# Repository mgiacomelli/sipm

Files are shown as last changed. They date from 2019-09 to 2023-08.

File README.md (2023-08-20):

**This page is obsolete.  A greatly improved design is available here: https://github.com/OpenSiPM/sipm-bias-control**

The updated design has higher dynamic range, lower noise, higher bandwidth and includes the bias generation, power supplies and low pass filter.  

# Introduction

These are the design files for the SIPM amplifier described in M. G. Giacomelli, "Evaluation of silicon photomultipliers for multiphoton and laser scanning microscopy," J. Biomed. Opt. 24, 1 (2019) available from https://www.spiedigitallibrary.org/journals/journal-of-biomedical-optics/volume-24/issue-10/106503/Evaluation-of-silicon-photomultipliers-for-multiphoton-and-laser-scanning-microscopy/10.1117/1.JBO.24.10.106503.full?SSO=1.  

The design is a relatively low cost, single photon sensitive fluorescense detector using the S14420 silicon photomultiplier from Hamamatsu, which is a TO-5 mounted detector with high QE from 500-700nm.  Compared to a PMT the S14420 has higher effective quantum efficiency (especially above 600nm) but higher dark counts.  

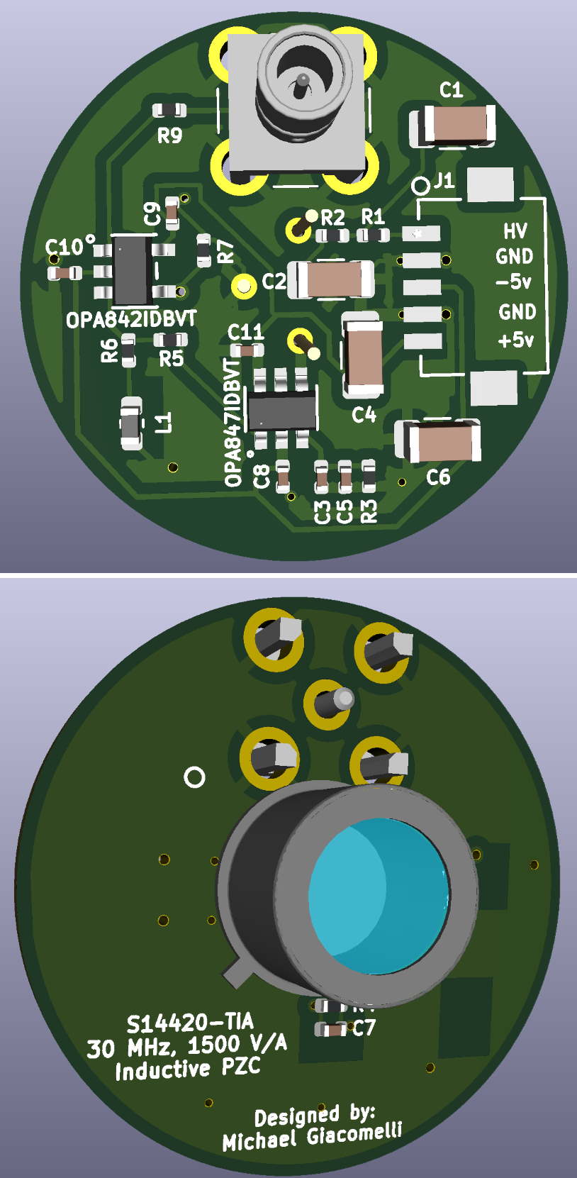
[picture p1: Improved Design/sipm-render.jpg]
Image of SIPM


# Files

The 'Old Gerbers' folder contains the exact gerber files used to manufacture the boards in the manuscript.  The Improved Design folder has KiCAD and gerber files for an updated version of that design that has a few improvements.  In addition, since the design files are present, you can make changes to the design as needed using the open source EDA software KiCAD.  If you only want to make a board, you can upload either set of Gerber files directly to JLCPCB, SEEED, etc.  

# Setting up KiCAD

This project was designed using the current development (5.99) branch of KiCAD, so you must be running that or newer.  Windows builds are available here: 
https://kicad-downloads.s3.cern.ch/index.html?prefix=windows/nightly/

# Ordering boards

Go to https://jlcpcb.com/ or https://www.seeedstudio.com/fusion_pcb.html or the service of your choice, upload the Gerber files, choose 2 layer, and pay.  At present prices, 10 boards will cost about 15-20 dollars shipped to most of the world.  

# Bill of materials

An interactive BOM tool is available here to make placing and ordering compnents easy:  http://htmlpreview.github.io/?https://github.com/mgiacomelli/sipm/blob/master/Improved%20Design/KiCAD/bom/ibom.html

In addition, you will need the matching power cable.  The part is DF13-5S-1.25C, and unless you have the matching crimp tool, you will need 5x H4BBT-10112-R8 pre-crimped leads.  I recommend getting multiple colors as mixing up the wires will destroy your board.  

# Assembly

The easiest way to assemble these boards is using solder paste and a reflow oven.  The inexpensive T-962 clones on Amazon will work fine for simple boards such as this.  Alternatively, they can also be manually soldered.  The design uses a mix of 0402 and larger parts, which can be challenging to solder with the wrong tools.  A ~0.6-1.2mm diameter chissel type soldering tip, high quality no clean flux such as amtech nc-559-v2-tf, 40/60 lead solder, and good tweezer such as Hakko CHP 5-SA or equivilent are strongly recommended if reflow is not used. These are inexpensive and readily available on Amazon. 

# Circuit design

Both the old and improved designs are a 1500 V/A transimpedance amplifier paired with a pole zero compensation (PZC) circuit.  Both PZCs have the same frequency cut on.  The old design uses a capacitive PZC.  While more obvious, this design is problematic because the capacitance of the PZC loads the amplifier.  The original design put an isolation resistor before the capacitance, but this design halves the gain and is less stable.  The improved design implements the same filter but using an inductor.  As a result the resistor and reactive element are flipped, meaning that the opamp is not directly connected to the reactive element and so the isolation resistor is not needed. Therefore gain is doubled.  Further since the PZC resistance is larger, stability is improved.  

# PZC

The values of L1, R5 and R6 define the PZC cut on and amplitude.  These values were near optimal for a previous board iteration, however, the PZC is very sensitive to the exact values so you may find that to hit very high bandwidth (40-50 MHz) or very flat pass band that the values must be adjusted.  Essentially the PZC is adding a gain that compensates for the frequency roll off caused by the RC time constant associated with the individual SIPM cell recharge through the quenching resistors, so adjusting L1 changes at what frequency the added gain kicks in, while changing the values of the resistors lets you change the strength of that gain.  By setting the values carefully, you can cancel out the recharge time of the individual APDs and greatly extend the bandwidth of the detector, often by a factor of 10 or more.  

A more intuitive explination of the PZC method is described in this article:
A. Gola, C. Piemonte, and A. Tarolli, "Analog circuit for timing measurements with large area sipms coupled to lyso crystals," IEEE Trans. Nucl. Sci. 60, 1296–1302 (2013).

# Low pass filter

It is important to add an external low pass filter, either in your ADC or inline with it to reject out of band noise.  If you do not have a suitable lowpass on your ADC, the minicircuits BLP-25 is a reasonable choice with relatively little group delay in the pass band:  https://www.minicircuits.com/WebStore/dashboard.html?model=BLP-25%2B

The bandwidth of a laser scanner is 0.312 times the scan velocity (in meters per second) divided by the spot size (also in meters).  It is a good idea to reduce the bandwidth of the detector as needed with a smaller low pass filter if you do not require 25 MHz at your scan speed.  This will reduce electronic noise.    

# Gain

Total transimpedance gain (as configured, you can adjust it) is 1500 ohms.  There is an additional factor of 2 gain in the OPA842 stage, but this merely compensates for the attenuation caused by the 50 Ohm output impedance.  In addition, the PZC attenautes by a factor of R6/R5 (about 8:1).  Thus peak ampltidue per photon at +5Vbr should be about 4.5mV.  

# Mounting

The entire board is 1 inch across and will mount in an SM1 lens tube:  https://www.thorlabs.com/newgrouppage9.cfm?objectgroup_id=3307

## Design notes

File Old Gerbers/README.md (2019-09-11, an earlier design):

# sipm
Design files for SIPM boards

BOM is here:  https://github.com/mgiacomelli/sipm/blob/master/TiaV3_BOM.xlsx

These are Gerber files for a SIPM+TIA detector board.  I'll update these eventually with a KiCAD design files when I have time to port over to KiCAD.  In the meantime, if you have questions or want to modify the design, contact me and I can help with that.

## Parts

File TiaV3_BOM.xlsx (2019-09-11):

Comment | Description | Name | Footprint | Quantity | Comment
0.10µF | CAP CER 0.1UF 200V X7R 0603 | C1, C5, C7, C9, C20, C21 | SMD-0603C | 6 | MUST use high voltage (>100V) caps for SIPM bias
3.9pF | CAP CER 3.9PF 50V NP0 0603 | C2 | SMD-0603C | 1
0.10µF | CAP CER 1UF 250V X7R 1206 | C3 | SMD-1206C | 1 | MUST use high voltage (>100V) caps for SIPM bias
4.7µF | CAP CER 4.7UF 25V X5R 1206 | C6, C10 | SMD-1206C | 2
100pF | CAP CER 100PF 50V NP0 0603 | C8 | SMD-0603C | 1
43pF | CAP CER 43PF 50V NP0 0603 | C23 | SMD-0603C | 1
0pf | Omitted | C? | SMD-0603C | 1
DF13-5P-1.25DSA | Power Connector | J1 | CON5_1X5_U_DF13 | 1 | Could substitute for through hole
SMB | SMB Straight Connector | P1 | SMB_V-RJ45 | 1
49.9 | RES SMD 49.9 OHM 1% 1/10W 0603 | R1 | SMD-0603-RES | 1 | Use thin film resistors only
1500 | RES SMD 1500 OHM 1% 1/10W 0603, RES SMD 750 OHM 1% 1/4W 0603 | R2, R3 | SMD-0603-RES | 2 | Use thin film resistors only
36 | RES SMD 36 OHM 1% 1/10W 0603 | R11, R? | SMD-0603-RES | 2 | Use thin film resistors only
422 | RES SMD 422 OHM 1% 1/10W 0603 | R20 | SMD-0603-RES | 1 | Use thin film resistors only
82 | RES SMD 82 OHM 1% 1/10W 0603 | R21 | SMD-0603-RES | 1 | Use thin film resistors only
50 | RES SMD 50 OHM 1% 1/10W 0603 | R22 | SMD-0603-RES | 1 | Use thin film resistors only
390 | RES SMD 490 OHM 1% 1/10W 0603 | R23 | SMD-0603-RES | 1 | Use thin film resistors only
75 | RES SMD 75 OHM 1% 1/10W 0603 | Riso | SMD-0603-RES | 1 | Larger values may be needed if unstable
SIPM | S14420-3025MG | S1 | TO-39 | 1
OPA847IDBVT | TI OPAMP | U2 | DBV6 | 1
OPA843IDBVT | Wideband, Low Distortion, Unity Gain Stable, Voltage Feedback Operational Amplifier, 7 to 12 V, -40 to 85 degC, 5-pin SOT23 (DBV5), Green (RoHS & no Sb/Br) | U? | TI-DBV5_N | 1 | Lower gain may be needed depending on A/D range, if R20/R21 < 4, switch to OPA842
Note: All parts are in the digikey catalog except for the SIPM

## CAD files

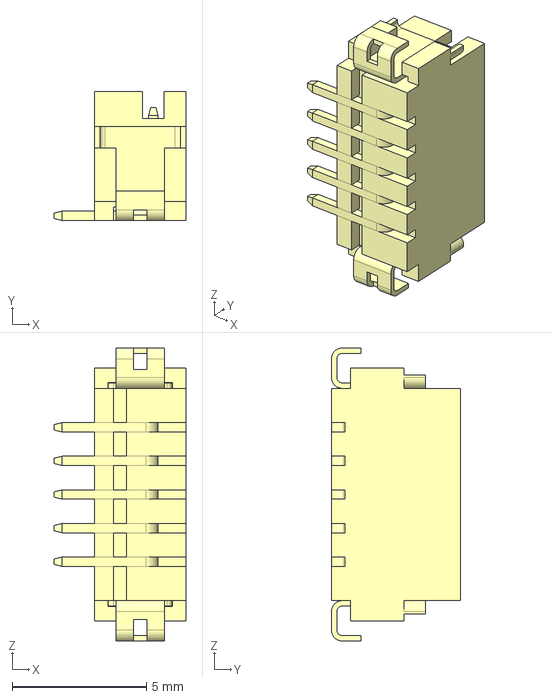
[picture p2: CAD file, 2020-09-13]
Improved Design/KiCAD/step/DF13C-5P-1.25V.stp
4.90 x 4.80 x 10.9 mm

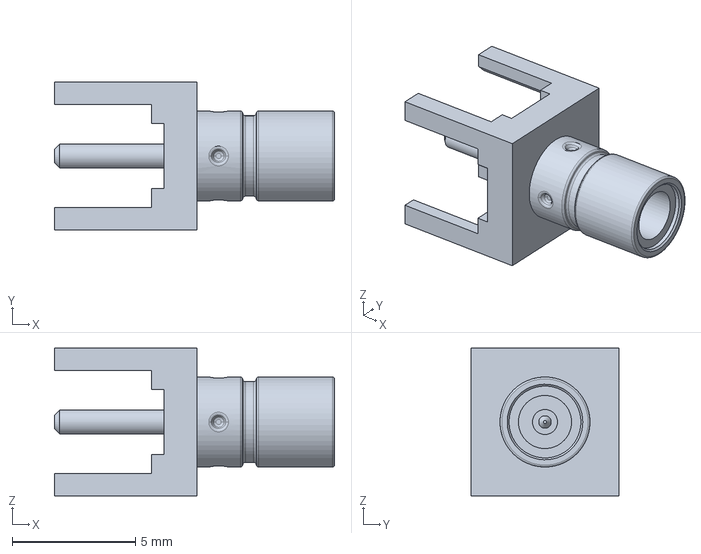
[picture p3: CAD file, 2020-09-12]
Improved Design/KiCAD/step/131-3701-261.stp
11.4 x 5.99 x 5.99 mm

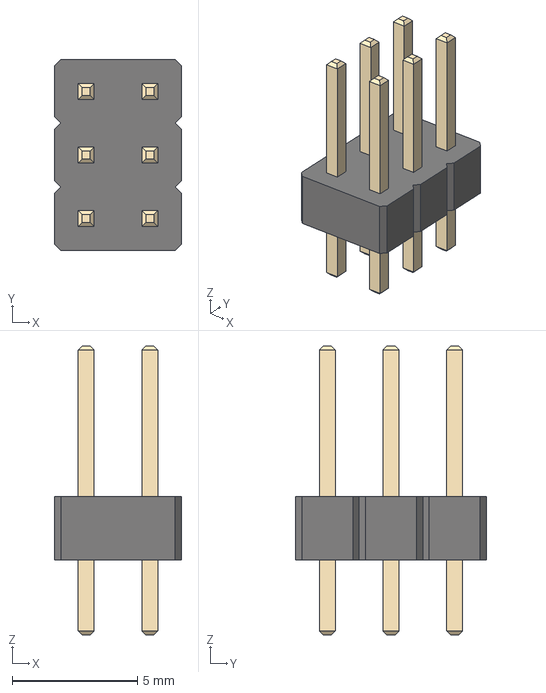
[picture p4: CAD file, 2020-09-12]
Improved Design/KiCAD/step/PinHeader_2x03_P2.54mm_Vertical.step
5.08 x 7.62 x 11.5 mm

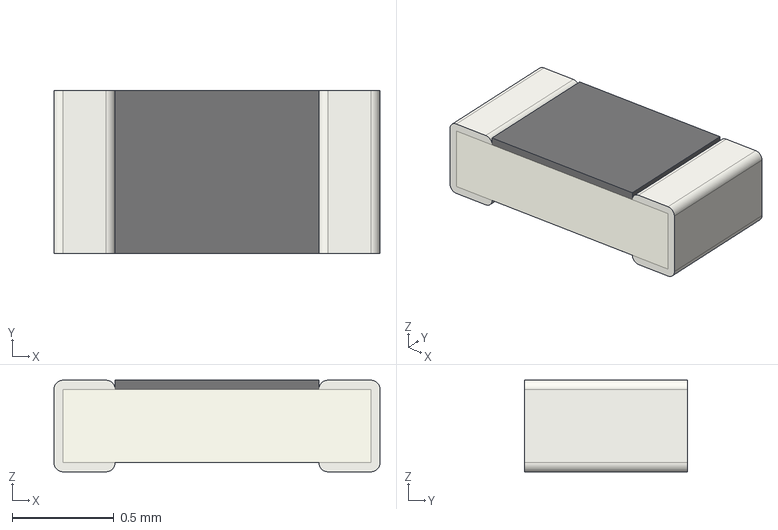
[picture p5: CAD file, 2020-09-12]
Improved Design/KiCAD/step/R_0603_1608Metric.step
1.60 x 0.8 x 0.45 mm

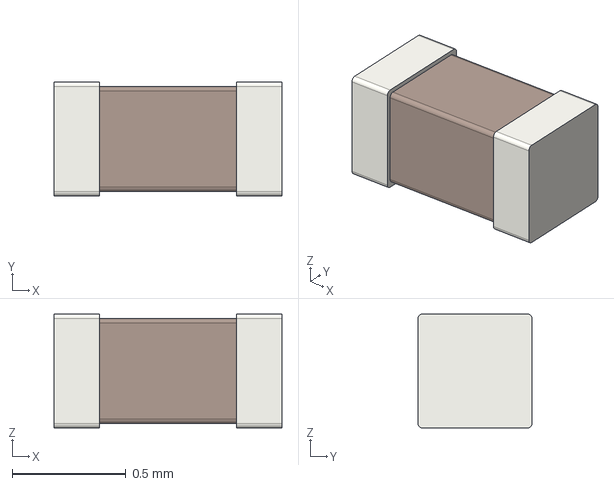
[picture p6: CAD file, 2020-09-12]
Improved Design/KiCAD/step/C_0402_1005Metric.step
1.00 x 0.5 x 0.5 mm

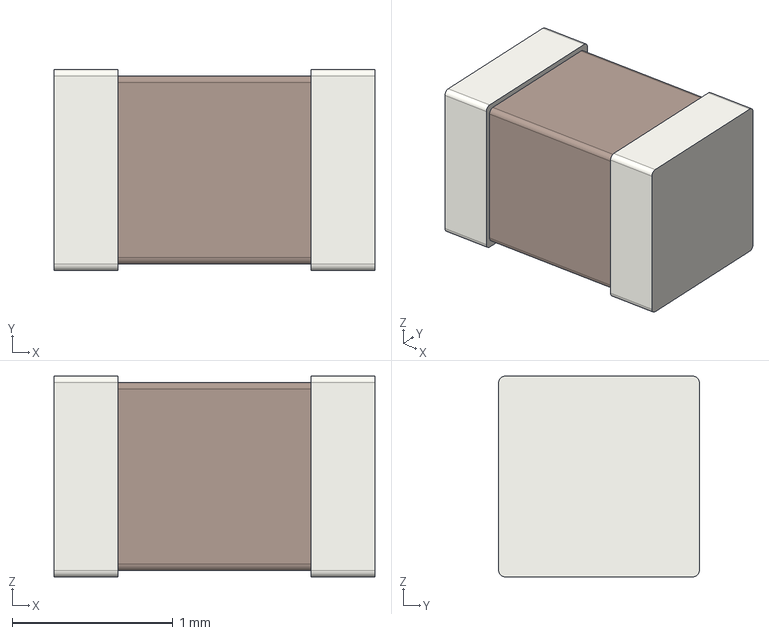
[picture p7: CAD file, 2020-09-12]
Improved Design/KiCAD/step/C_0805_2012Metric.step
2.00 x 1.25 x 1.25 mm

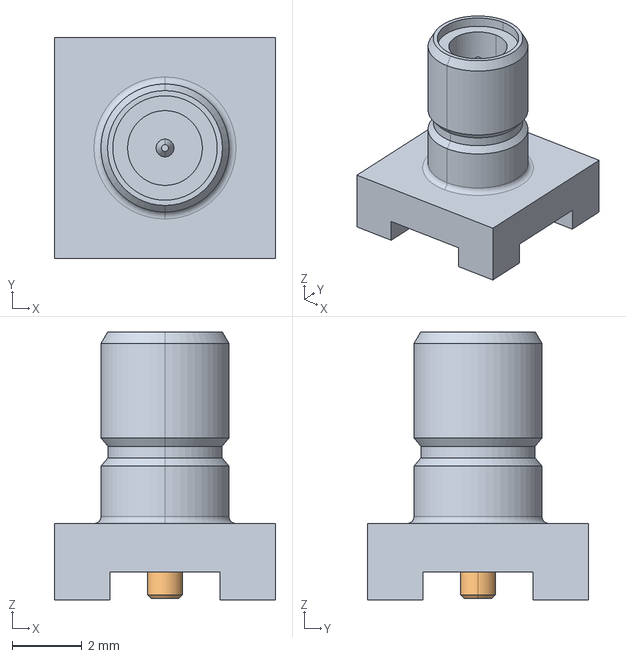
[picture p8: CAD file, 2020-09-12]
Improved Design/KiCAD/step/c-1-1337604-0-d-3d.stp
6.35 x 6.35 x 7.70 mm

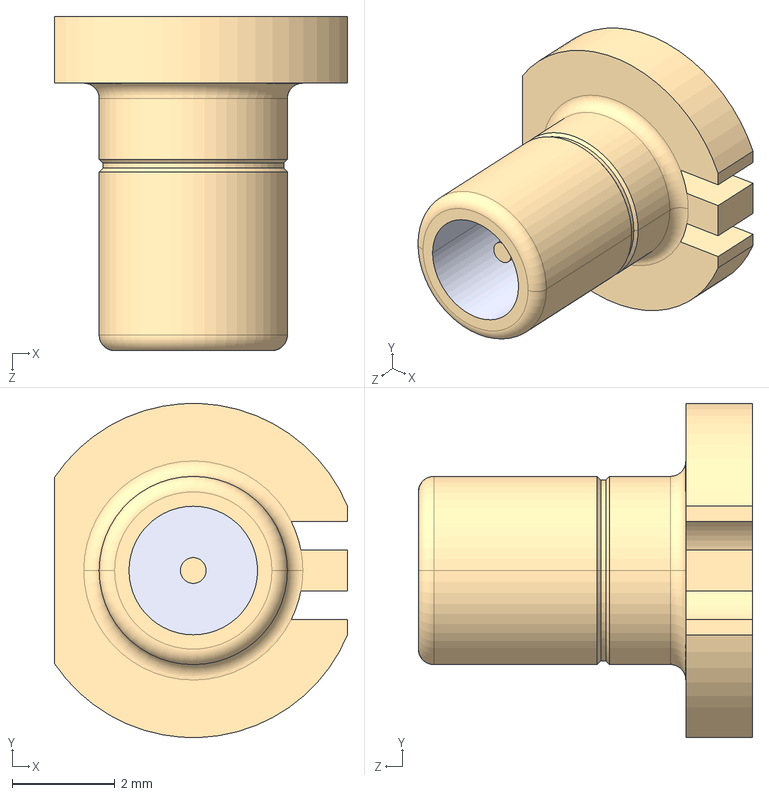
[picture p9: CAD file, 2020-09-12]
Improved Design/KiCAD/step/SMBR004D00.step
5.70 x 6.49 x 6.50 mm

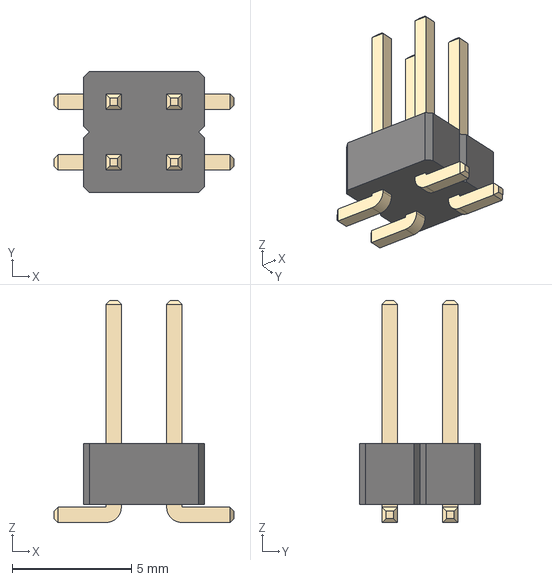
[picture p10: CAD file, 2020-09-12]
Improved Design/KiCAD/step/PinHeader_2x02_P2.54mm_Vertical_SMD.step
7.54 x 5.08 x 9.30 mm

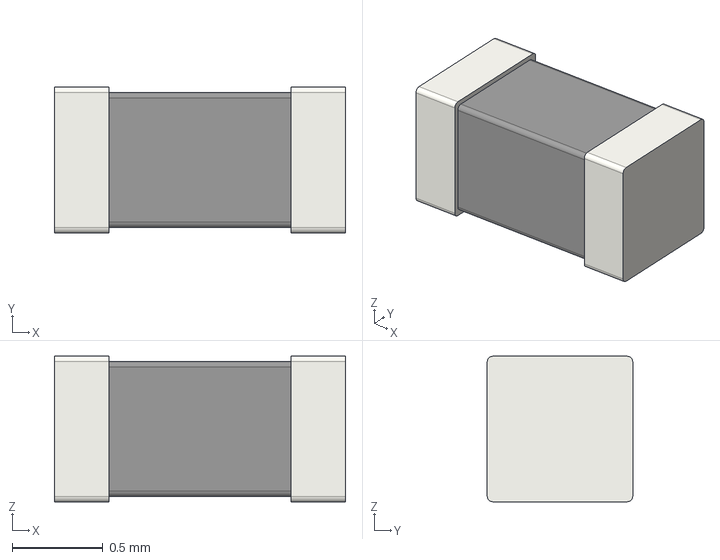
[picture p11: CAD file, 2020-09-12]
Improved Design/KiCAD/step/L_0603_1608Metric.step
1.60 x 0.8 x 0.8 mm

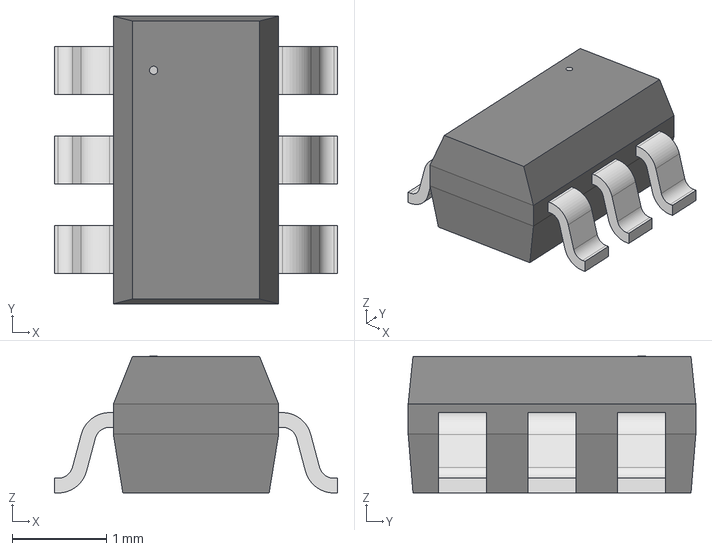
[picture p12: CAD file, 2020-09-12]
Improved Design/KiCAD/step/DBV6.step
3.00 x 3.05 x 1.45 mm

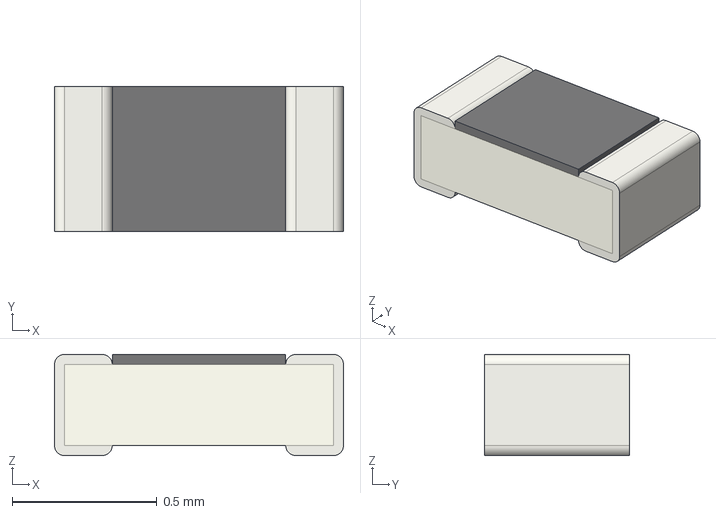
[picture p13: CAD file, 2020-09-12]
Improved Design/KiCAD/step/R_0402_1005Metric.step
1.00 x 0.5 x 0.35 mm

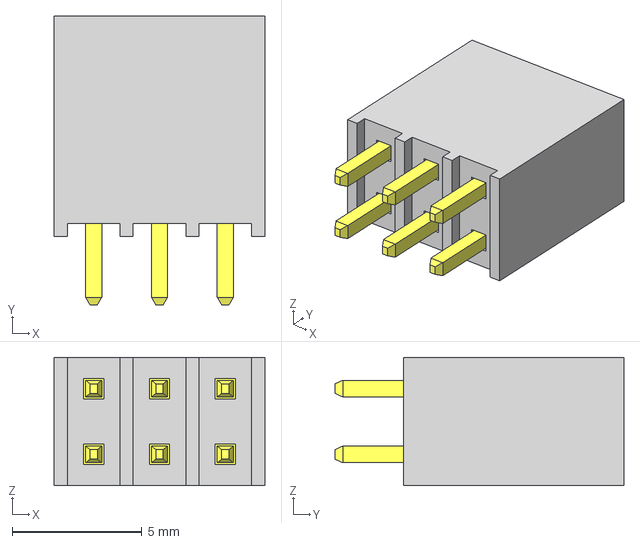
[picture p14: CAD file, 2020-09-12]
Improved Design/KiCAD/step/SSQ-103-01-G-D.step
8.13 x 11.2 x 4.95 mm
_T1SSQ-103-01-G-D
_P2SSQ-103-01-G-D

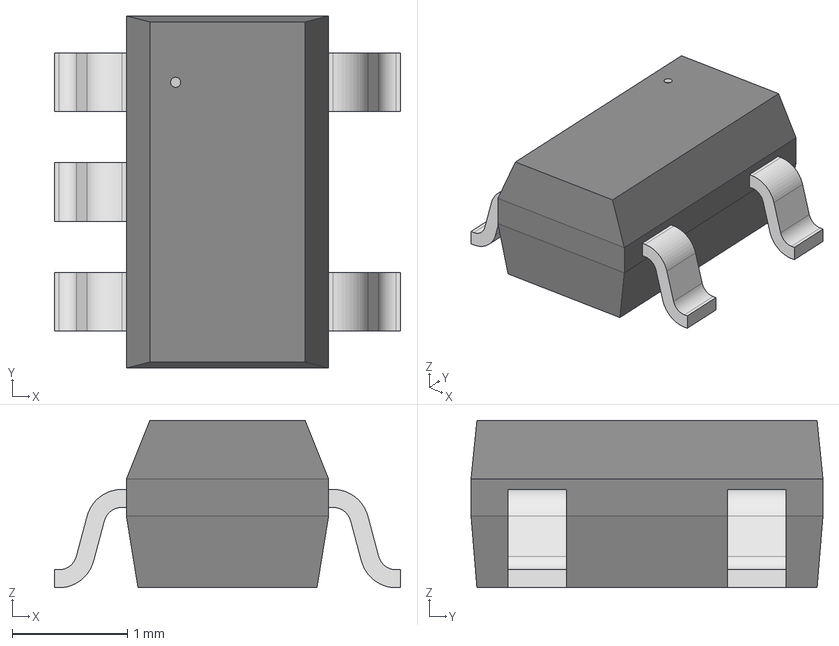
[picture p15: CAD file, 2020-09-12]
Improved Design/KiCAD/step/DBV5.step
3.00 x 3.05 x 1.45 mm

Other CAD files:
Improved Design/KiCAD/step/C_0603_1608Metric.step
Improved Design/KiCAD/step/73415-2061.stp
Improved Design/KiCAD/step/SMBR004D00.SLDPRT

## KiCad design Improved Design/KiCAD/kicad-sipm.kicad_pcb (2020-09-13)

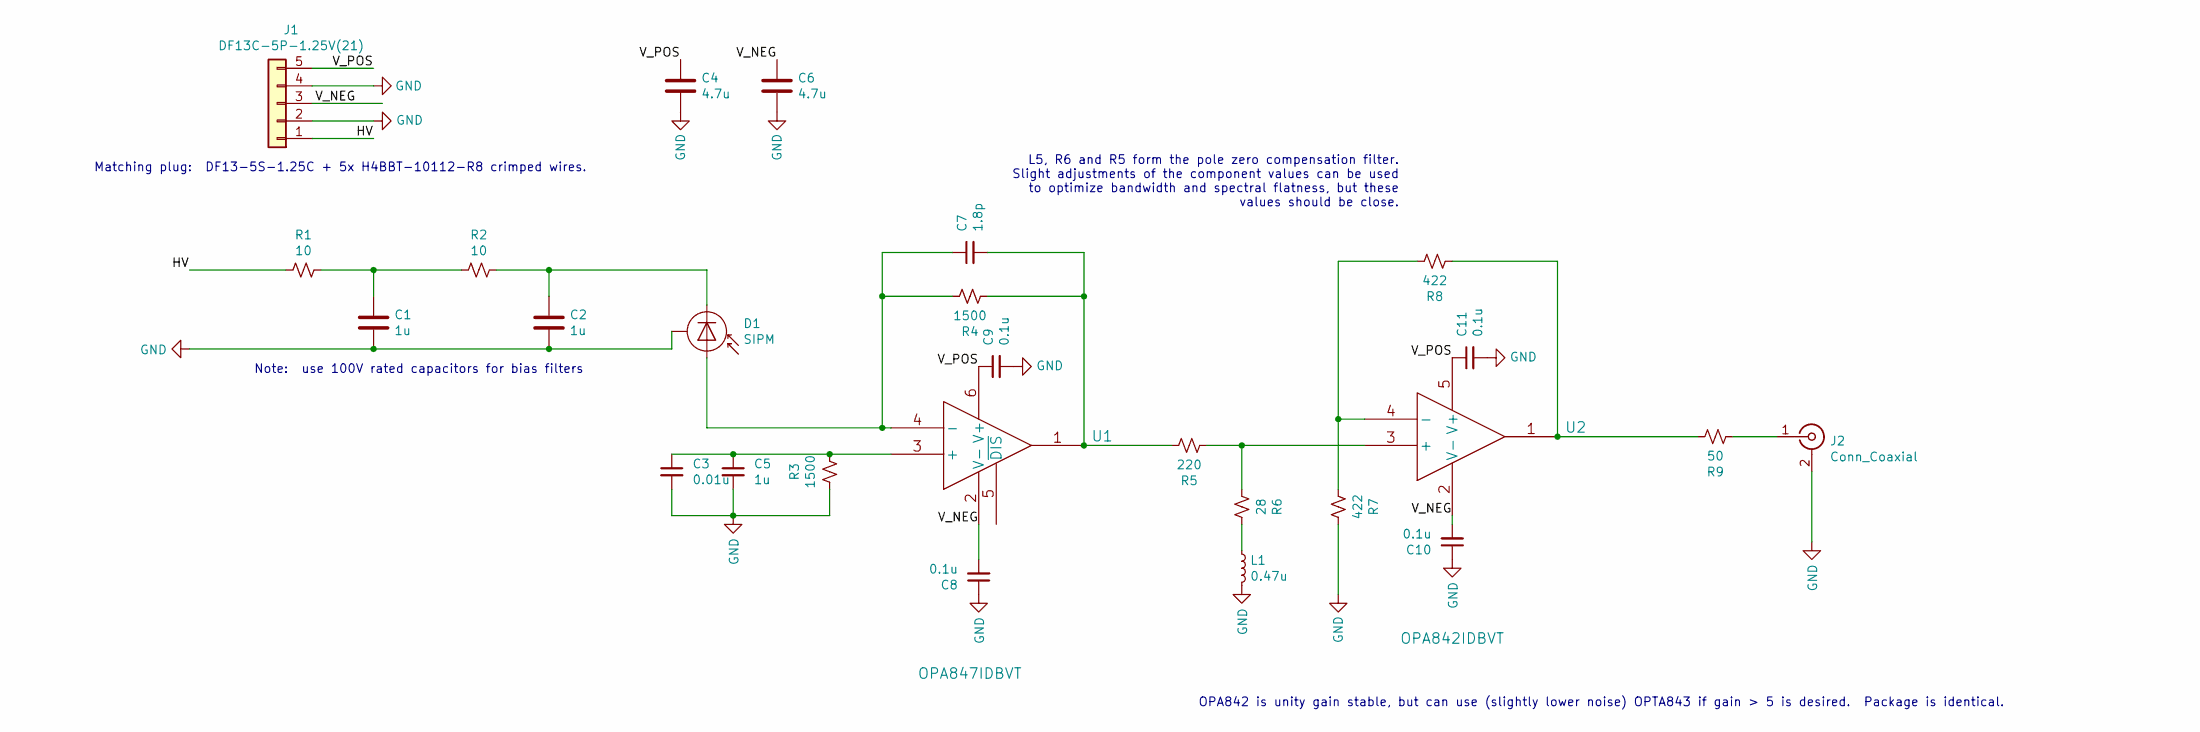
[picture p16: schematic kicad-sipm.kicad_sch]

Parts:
C1, C2: 1u; C_1206_3216Metric
C3: 0.01u; C_0402_1005Metric
C4, C6: 4.7u; C_1206_3216Metric
C5: 1u; C_0402_1005Metric
C7: 1.8p; C_0402_1005Metric
C8, C9, C10, C11: 0.1u; C_0402_1005Metric
D1: SIPM; S14420
J1: DF13C-5P-1.25V(21); DF13C-5P-1.25V21; Digikey Part H126001CT-ND
J2: Conn_Coaxial; SMB_Jack_Vertical
L1: 0.47u; L_0603_1608Metric
R1, R2: 10; R_0402_1005Metric
R3, R4: 1500; R_0402_1005Metric
R5: 220; R_0402_1005Metric
R6: 28; R_0402_1005Metric
R7, R8: 422; R_0402_1005Metric
R9: 50; R_0402_1005Metric
U1: OPA847IDBVT
U2: OPA842IDBVT; OPA843IDBVT

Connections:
/HV: J1.1, R1.1
/V_NEG: C6.1, C8.2, C10.2, J1.3, U1.2 (V-), U2.2 (V-)
/V_POS: C4.1, C9.1, C11.1, J1.5, U1.6 (V+), U2.5 (V+)
GND: C1.2, C2.2, C3.2, C4.2, C5.2, C6.2, C8.1, C9.2, C10.1, C11.2, D1.3 (CASE), J1.2, J1.4, J2.2 (Ext), L1.2, R3.1, R7.2
unnamed: C1.1, R1.2, R2.1
unnamed: C2.1, D1.1 (K), R2.2
unnamed: C3.1, C5.1, R3.2, U1.3 (+)
unnamed: C7.1, D1.2 (A), R4.2, U1.4 (-)
unnamed: C7.2, R4.1, R5.2, U1.1
unnamed: J2.1 (In), R9.1
unnamed: L1.1, R6.2
unnamed: R5.1, R6.1, U2.3 (+)
unnamed: R7.1, R8.2, U2.4 (-)
unnamed: R8.1, R9.2, U2.1

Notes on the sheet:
Note: use 100V rated capacitors for bias filters
Matching plug: DF13-5S-1.25C + 5x H4BBT-10112-R8 crimped wires.
OPA842 is unity gain stable, but can use (slightly lower noise) OPTA843 if gain > 5 is desired. Package is identical.
L5, R6 and R5 form the pole zero compensation filter. Slight adjustments of the component values can be used to optimize bandwidth and spectral flatness, but these values should be close.

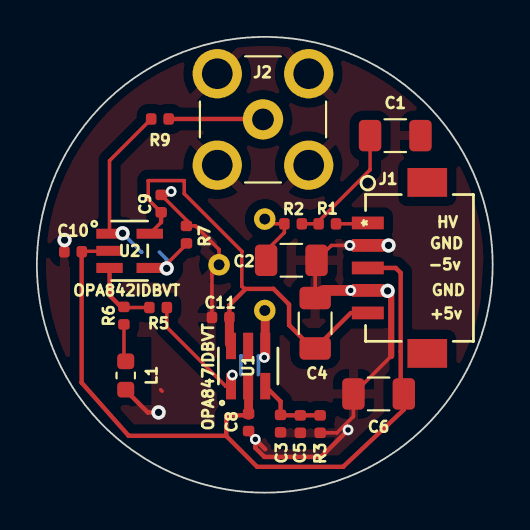
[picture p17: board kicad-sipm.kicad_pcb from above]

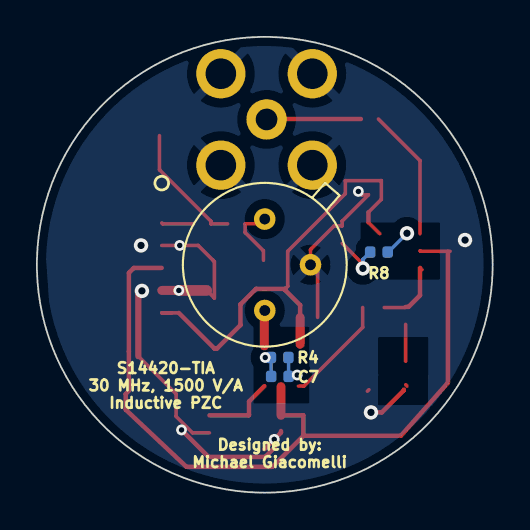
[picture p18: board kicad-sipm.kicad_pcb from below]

Board: 2 copper layers, 25.3 x 25.3 mm, 26 parts (4 on the bottom side), 14 nets.

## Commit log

2019-09-09 Check in Gerber files for the TIA v3 PCB design.
    [smd_tia_schematic.GBL, smd_tia_schematic.GBO, smd_tia_schematic.GBS, smd_tia_schematic.GKO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]
2019-09-11 Add BOM for the TIAv3 project.
    [TiaV3_BOM.xlsx]
2020-09-12 Add KiCAD design files for updated TIA design
    [131-3701-261.stp, 73415-2061.stp, C_0402_1005Metric.step, C_0603_1608Metric.step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]
2020-09-12 Set project output to JLCPCB recommended settings
    [kicad-sipm.kicad_pcb]
2020-09-12 Commit Gerbers and fix some labeling mistakes
    [kicad-sipm-B_Cu.gbr, kicad-sipm-B_Mask.gbr, kicad-sipm-B_SilkS.gbr, kicad-sipm-Edge_Cuts.gbr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]
2020-09-12 Add part number for the pin header and the matching plug
    [kicad-sipm.kicad_sch]
2020-09-12 Update labels one more time.
    [kicad-sipm.kicad_pcb]
2020-09-13 Correct PZC values
    [kicad-sipm.kicad_sch]
2020-09-13 Add 3d model for connector
    [DF13C-5P-1.25V.stp, kicad-sipm.kicad_pcb]

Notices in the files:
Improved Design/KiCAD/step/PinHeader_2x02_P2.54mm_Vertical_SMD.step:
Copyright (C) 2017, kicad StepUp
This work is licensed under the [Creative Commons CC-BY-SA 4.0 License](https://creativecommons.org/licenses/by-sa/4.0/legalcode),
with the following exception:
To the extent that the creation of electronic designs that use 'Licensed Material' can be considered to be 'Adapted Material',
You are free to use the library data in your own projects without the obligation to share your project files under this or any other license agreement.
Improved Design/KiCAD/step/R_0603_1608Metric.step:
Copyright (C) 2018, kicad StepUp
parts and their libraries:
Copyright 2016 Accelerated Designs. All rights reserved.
